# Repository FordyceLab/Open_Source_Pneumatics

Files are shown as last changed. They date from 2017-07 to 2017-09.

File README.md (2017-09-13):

# Open_Source_Pneumatics
An Open-Source, Fully Programmable Pneumatic Setup for Universal Microfluidic Operation and Automated Control

This repository includes Build Guides (All Modules), Build Description and Overview (Manuscript), Customization Options (see Figures), all Design Files (Design File Folder) and a Bill of Materials for 3 build options of an open source microfluidic pneumatic controller. 

We have described this controller in our BioArXiv release which can be found here: 

http://www.biorxiv.org/content/early/2017/08/13/173468

DOI: https://doi.org/10.1101/173468

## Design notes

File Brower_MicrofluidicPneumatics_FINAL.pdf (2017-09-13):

Article Submission: HardwareX Article Template

Title: An Open-Source, Programmable Pneumatic Setup for Operation and Automated Control of Single- and Multi-Layer Microfluidic Devices

Authors: Kara Brower¹,4,5, Robert Puccinelli²

, Craig J. Markin³

, Tyler C. Shimko²

, Scott A. Longwell¹
,
Bianca Cruz⁶

, Rafael Gomez-Sjoberg⁷

*, and Polly M. Fordyce¹,2,4,5,7 *

Affiliations: 1

Department of Bioengineering, ²

Department of Genetics, ³
Department of Biochemistry,

4

Chem-H Institute, ⁵
Stanford Microfluidic Foundry, Stanford University, Stanford CA 94305. 6 Department of Physics and Astronomy, California State Polytechnic University Pomona, Pomona CA 91768. 7
Chan Zuckerberg Biohub, San Francisco CA 94158.

*These authors contributed equally to this work.

Contact email: Polly Fordyce, Ph.D., pfordyce@stanford.edu

Abstract: Microfluidic technologies have been used across diverse disciplines (e.g. high-throughput biological measurement, fluid physics, laboratory fluid manipulation) but widespread adoption has been limited due to the lack of openly disseminated resources that enable non-specialist labs to make and operate their own devices. Here, we report the open-source build of a pneumatic setup capable of operating both single and multilayer (Quake-style) microfluidic devices with programmable scripting automation. This setup can operate both simple and complex devices with 48 device valve control inputs and 18 sample inputs, with modular design for easy expansion, at a fraction of the cost of similar commercial solutions. We present a detailed step-by-step guide to building the pneumatic instrumentation, as well as instructions for custom device operation using our software, Geppetto, through an easy-to-use GUI for live on-chip valve actuation and a scripting system for experiment automation. We show robust valve actuation with near real-time software feedback and demonstrate use of the setup for high-throughput biochemical measurements on-chip. This open-source setup will enable specialists and novices alike to run microfluidic devices easily in their own laboratories.

Keywords: Microfluidics, pneumatics, laboratory automation, biochip, bioMEMs, biohacking, fluid handling, micro total analysis systems (µTAS), Quake-style valves

Specifications table
Hardware name | An Open-Source, Programmable Pneumatic Setup for Operation and Automated Control of Single- and Multi-Layer Microfluidic Devices Geppetto (Python-based solenoid valve control software with GUI) Geppetto CLI (Python-based solenoid valve software with command line scripting for experiment automation)
Subject area | • Engineering and Material Science • Biological Sciences (e.g. Microbiology and Biochemistry) • General

Hardware type | • Biological sample handling and preparation
Open Source License | Pneumatics Instrumentation: GPL License Geppetto Software: MIT License
Cost of Hardware | Variable, dependent on user customization Full Build: $10,380. Abridged Build: $4,455. Manual Build: $2,110. Additional Modification Builds Costs shown in Table 1
Source File Repository | Github: github.com/FordyceLab/Open_Source_Pneumatics Supplementary Materials (In Article)

### 1. Introduction

Microfluidic technologies enable the precise control and manipulation of fluid at the sub-millimeter scale [1]. Simple, single layer microfluidic devices with channels etched in glass or patterned into soft polymers (e.g. polydimethylsiloxane, or PDMS) have facilitated the study of small-scale fluid phenomena, automated sample loading and common laboratory tasks, and been used for high-throughput compartmentalization of biological reactions [2-9]. More complex multilayer microfluidic devices with monolithic soft polymer valves (also known as Quake-style valves [10,11]) have empowered additional research and commercial applications, including on-chip cell culture and tissue engineering [12], crystallization condition scanning [13-15], single cell analysis [16-18], high-throughput biochemical analysis [19-21], hydrogel engineering [22-24], and complex fluid handling tasks [11,25].
These multilayer microfluidic devices are typically fabricated in a two-layer geometry, where each layer is made by conventional soft lithography [10]. The ‘flow layer’ contains channels to load and transport samples. The ‘control layer’ contains a series of channels that create and control pneumatically-actuated valves. The two layers are separated by a thin polymer membrane. A valve is formed when flow and control channels of an appropriate size and shape cross [26]. When a control channel is pressurized, the thin membrane deflects into the crossing flow channel to modulate its flow. Both layers require their own set of input lines to interface with on-chip inlets. For complex chips with many control valves, a computer-controlled bank of solenoid valves is typically used to automate control of applied pressure to the valves.
While multilayer devices can serve as powerful tools for a broad range of biological systems [5,27-29], their widespread adoption has been limited, likely because few detailed open-source protocols and designs for building an automated pneumatic control systems have been published [3,30,31]. Previously, our group worked in conjunction with the Stanford Microfluidic Foundry to publish an open protocol that describes in detail how to fabricate custom multilayer microfluidic devices [32]. In this report, we continue the project of disseminating how-to knowledge on microfluidics by offering designs and detailed step-by-step build instructions for a flexible pressure-driven pneumatic setup that can control both fluid flow and integrated on-chip valves.
The primary pneumatics control system described here allows for automated, programmable control of single and multi-layer microfluidic devices with 48 control lines and 18 individually-addressable flow lines. We present customization options and instructions to build setups from 8 – 96 control lines and 6 – 48 flow lines using this base build. This setup confers several advantages to commercial alternatives including:
- flexible application programming and automation
- remote control to allow experiments to be controlled and monitored outside the lab
- extremely fast valve response times (using Modbus-pulsed solenoid valves)
- very low cost-per-input ratios (both control and flow channel inputs)

The build is modular and easy to customize for a user’s specific needs. We present two modified builds in a later section of the paper for lower complexity control, including a low-cost fully manual control configuration. Previous versions and variants of this setup, originating from the early days of the Stanford Microfluidic Foundry [33], have been used in tens of laboratories resulting in over a hundred peer-reviewed publications ([12,20-23,34,35] are some examples). However, full build details have never been published. Here, we describe the latest optimization of the pneumatic control system in detail to provide a complete tool kit that will allow even labs with little engineering expertise to build all of the instrumentation required for automated microfluidic control.

### 2. Hardware description

The open-source pneumatic setup and software (Figure 1) described here can be used for both manual and fully programmable pneumatic control of most PDMS-based microfluidic devices. Our associated software, Geppetto, has both an interactive GUI for manipulating device valves and visualizing their current state (open or closed) as well as command line scripting functionality for automating experiments.
We present 3 build options for the microfluidic pneumatic control system, as listed below. This setup can additionally be expanded for up to 96 control lines and up to 48 flow lines. Control inputs need not correspond to the actual number of valves on the device - only the number of valves needing independent actuation. Typical multilayer microfluidic devices operate with 10 – 15 control lines and 10 – 15 sample lines, even for complicated tasks, but this build can accommodate devices with more or fewer inputs or the need to run multiple devices simultaneously on the same setup.

### 2.1. Build Options

In this paper, we present 3 options for building a microfluidic pneumatic setup:

Option 1: A full build for 18 flow lines and 48 individually addressable solenoid valves to drive 48 control lines for fully automated, programmable and remote operation of complex devices or multiple devices

Option 2: An abridged build for 6 flow lines and 8 individually addressable solenoid valves to drive 8 control lines for fully automated, programmable and remote operation of simpler devices

Option 3: A low-cost build for manual control of 18 flow lines and 12 control lines

The main text will describe the build for Option 1. The build is modular and can be easily modified to the simpler builds of Options 2 and 3 to reduce time and cost, if only limited or manual control of microfluidic devices is needed.

### 2.2. Module Overview

The pneumatics control system is built in 5 Modules which are divided by manual and automated control capabilities. Options 1 and 2 require all 5 Modules. The manual build, Option 3, requires a modified version of only Modules 1 and 2. The builds for Options 2 and 3 are presented in a Modifications and Customization Section.

The Modules are as follows:

- Module 1: Base Board, Pressure Regulator Manifolds, and Flow Lines
- Module 2: Filter Assembly
- Module 3: Control Solenoid Valve Manifolds
- Module 4: Control Reservoir Loading Assembly
- Module 5: Digital Modbus Control

Manual Control Modules

This pneumatic setup employs pressure-driven flow control. Microfluidic devices, in general, can be operated either by pressure-drive flow (using constant pressure at the input) or volumetric flow (forcing a set flow rate at the input, as a syringe pump does). Volumetric flow results in unknown pressures inside the flow channels, which makes it difficult to ensure that on-chip valves close reliably and can lead to device delamination. This setup uses pressure-driven flow because it requires little additional equipment beyond common laboratory compressed air sources and provides robust valve actuation on-chip.

Controlling pressure-driven flow rates and actuating on-chip pneumatic valves requires a device-specific pressure range: too little pressure and valves don’t close properly, too much pressure and devices can delaminate or become otherwise damaged. Compressed air (from a house air supply, cylinder or compressor) provides a convenient and quiet pressure source but must be adjusted to the correct pressure for microfluidic devices using regulators. Module 1 (Base Board, Pressure Regulator Manifolds, and Flow Lines) describes the base build for the pneumatic assembly to control input pressures. It contains a base board that mounts regulators for controlling both flow lines and control line manifold pressures as well as fluidic components for sample introduction or manual control of integrated on-chip valves.

Module 2 describes how to connect a filtering assembly to the compressed air source to prevent device contamination and/or clogging of the air regulators.

Automated Control Modules

Automation of microfluidic valve actuation enables a wide range of additional assays and remote device control but requires additional control hardware. To control on-chip valves, we employ 24V, three-way, normally open solenoid valves which toggle between an ‘open’ pressurized state (with pressure from the control manifold regulators in Module 1) and a ‘closed’ atmospheric pressure state to close or open on-chip valves, respectively. These solenoid valves are used to pressurize or depressurize water within a reservoir directly connected to control lines, thereby providing individually-addressable control of each control line. Groups of eight of these solenoid valves are coupled to a plastic manifold containing eight water reservoirs connected to eight chip control lines. We call this assembly a control manifold; these manifolds are built in Module 3 (Control Solenoid Valve Manifolds). Module 4 (Control Reservoir Loading Assembly) adds on a large volume water bottle for easy loading and refilling of the water reservoirs in the control manifold. Finally, Module 5 (Digital Modbus Control) describes the electrical connections between the solenoid valves and a microcontroller (the ‘WAGO’ fieldbus controller) to allow values to be digitally controlled by the user via a computer.

Pneumatic Control System Operation

Combined, these modules constitute all the components and connections necessary to provide pressure-driven flow control and actuate integrated on-chip valves of microfluidic devices. Initial setup of the system for experimental use is described in the Operation Device Guide.

Figure 1. Photograph of a completed pneumatic build (Option 1) with all 5 build modules.

Figure 2. Overall setup schematic with parts designated by letter and number (as referenced to the Bill of Materials).

While at first glance this setup may seem complicated, we have built multiple setups with researchers of all technical backgrounds with little to no engineering training. Each module is accompanied by a schematic, parts list and illustrated step-by-step build instructions (Build Guides) that are included in the Supplemental Material of this report. The total build takes 1.5 days from start to device testing and is easily managed with 1-2 researchers and common laboratory tools.

2.3.Advantages of an Open-Source Build

Building an open-source pneumatic microfluidic control system has three main advantages to both academic researcher and small companies. First, open source builds are flexible and can be easily modified for a laboratory’s needs [30,36]. For instance, this paper describes two easily modified options from the base build in the Modification and Customization Section. Second, this build is highly modular; if a component fails or the user prefers a different alternative to a given module (i.e., using an Arduino as opposed to a WAGO PLC), parts can easily be swapped or exchanged. This can be contrasted with commercial closed-source pumps and instruments where exchanges and repairs are often costly and time-consuming. Lastly, the control system described here is significantly cheaper per input than existing solutions, as discussed below.

2.4.Note on Associated Build Costs

This setup has a significantly reduced cost compared to commercial alternatives for the same number of independent input controls. Table 1 shows the cost of hardware for Build Option 1 (full build, 48 control lines), Build Option 2 (modified programmable build, 8 control lines) and Build Option 3 (fully manual, 12 control lines). The most expensive components are the solenoid valve arrays and WAGO fieldbus digital control modules, which scale directly with the number of independently-addressable control lines needed, as shown in Table 1. While the cost of these programmable setups can be significant ($4,455 to $10,380 dependent on number of inputs), commercial solutions cost between $1,500 (lower-end microfluidic syringe pumps) to $5,550 (high end pressure-driven pumps, e.g. Dolomite P-PumpTM) per independent input. Consequently, obtaining a similarly programmable pneumatic system for many inputs from commercial suppliers would be > 10X more expensive in the current market than the build described here.

Build Option | Cost of all associated hardware
#1: Full Programmable Build (48 control lines, 18 flow lines) | $10,379.65

#2: Abridged Programmable Build (8 control lines, 6 flow lines) | $4,455.14

#3: Manual Build (12 control lines, 18 flow lines) | $2,110.50

Table 1 Cost of Hardware for the different Build Options. See Supplemental Bill of Material for itemized costs.

2.5.Hardware Summary

- This build describes a pressure-driven pneumatic setup for single- and multi-layer microfluidic device operation. Devices can be operated manually or digitally, enabling remote control.
- The user can customize the number of flow inputs (up to 48) and the number of control inputs (up to 96) for their application.
- The associated software for digital valve control, Geppetto, includes a GUI for fast valve actuation and visualization of current valve states as well as an easy way to script experiments for automated control.
- The build description includes design files to be cut, printed, or machined, as well as overview instructions and step-by-step build guides to construct the setup in 5 different modules, a bill of materials and individual parts list by module, software operation instructions, and an example case for easy construction. These resources can also be found on our Github (https://github.com/FordyceLab/Open_Source_Pneumatics).
- The final setup is ~48” x 24” including the control computer and can be mounted on an optical breadboard, lab bench, or any workspace with either screws or C-clamps.

### 3. Design Files

3.3.Design Files Summary

The following design files are necessary to complete this build. Downloads of parts in editable file formats (e.g. AutoDesk 360 files) are available on the GitHub repository under the Designs folder.

Design file name | File type | Open source license | Location of the file
System Schematic | PDF | GPL | Available with the article
Bill of Materials, Detailed with Links | XLSX | GPL | Available with the article
Build Guides | PDF (multiple) | GPL | Available with the article
Base Board (backboard-full) | PDF DXF | GPL | Github:github.com/FordyceLab/Open_Source_Pneumatics
Flow Control Manifolds (stopcock-mount) | STL | GPL | Github:github.com/FordyceLab/Open_Source_Pneumatics
Water Reservoir Stand (reservoir-stand) | PDF DXF STL | GPL | Github:github.com/FordyceLab/Open_Source_Pneumatics
Control Water Reservoir (reservoir) | PDF DXF | GPL | Github:github.com/FordyceLab/Open_Source_Pneumatics
Geppetto Geppetto CLI | Python code | MIT | Github: https://github.com/FordyceLab/geppetto Github: https://github.com/FordyceLab/geppetto-cli

Table 2 Design File Summary.

3.4.Description of Design Files

Build Instructions

System_schematic_pneumatics.pdf – Schematic of all parts organized by build module Bill_of_Materials_pneumatics.xlxs – Multi-sheet parts list, global and by-module (includes modification and custom build Options 2 and 3).

Build and Operation Step-by-Step Guides
Module_1_Base_Build_Guide.pdf – Guide for the Module 1 build Module_2_Filter_Assembly_Guide.pdf – Guide for the Module 2 build Module_3_Valve_Manifolds_Guide.pdf – Guide for the Module 3 build Module_4_Control_Loading_Guide.pdf – Guide for the Module 4 build Module_5_WAGO_Guide.pdf – Guide for the Module 5 build
Operation_Start_Guide.pdf – Instructions for setup initialization and first-time use. Device_Operation_Guide.pdf – Instructions for device operation and experimental automation.

Laser Cut Parts
Base Board: backboard-full (PDF specifications; DXF for submission to 3rd party) – 28” x 20” backboard to which most components are mounted. Fabrication: ¼” aluminum or acrylic stock. Holes can be drilled or laser cut. Threaded holes hand-tapped as per specifications.
Water Reservoir Stand: reservoir-stand (PDF specifications; DXF for submission to 3rd party; STL for 3D printing) – Mounting stand for control manifold water reservoirs. Fabrication: ¼” aluminum or acrylic stock. Threaded holes hand-tapped as per specifications. Alternatively, can be ordered from local plastic suppliers/3rd party, or 3D printed on printers with a sufficiently large workspace.

Optional Modified Laser Cut Parts
Base Board Alternatives:

backboard-left (PDF specifications; DXF for submission to 3rd party) – The left 10.5” of backboard-full. Its reduced size enables fabrication on laser cutters with smaller workspaces. It should be used with backboard-right; if this component is used, backboard-full is not needed. backboard-right (PDF specifications; DXF for submission to 3rd party) – The right 17.5” of backboard-full. Same specifications as above.
backboard-left-lc (PDF for laser cutter) – Variation of backboard-left specifically for direct conversion to a Universal Laser Systems file format (lines are 0.02 mm wide, [255,0,0] RGB). Please verify that the file format is compatible with your laser cutter.
backboard-right-lc (PDF for laser cutter) – Variation of backboard-right specifically for direct conversion to a Universal Laser Systems file format (lines are 0.02 mm wide, [255,0,0] RGB). reservoir-stand-lc (PDF for laser cutter) – Variation of reservoir-stand specifically for direct conversion to a Universal Laser Systems file format (lines are 0.02 mm wide, [255,0,0] RGB).

Machined Parts
Control Water Reservoirs: reservoir (PDF specifications; DXF for submission to 3rd party) – Control manifold reservoirs used to hold water for control lines. Fabrication: 1” acrylic stock. Custom machined in-house or by 3rd party.

3D Printed Parts

Flow Control Manifold: stopcock-mount (STL for printing) – Mount for 3 stopcocks that control flow line pressurization. Fabrication: ABS plastic or similar.

Open-Source Software
Geppetto (Github Repository) – Python pneumatic control software with Kivy GUI and optional Windows binary. A Read Me file and all code dependencies are included in the repository unless noted. Example files are included in the repository.

Geppetto CLI (Github Repository) – Python pneumatic control software for command line scripting (command line integration, CLI) to automate experiments. A Read Me file and all code dependencies are included in the repository. Example files are included in the repository.

### 4. Bill of Materials

4.3.Master Bill of Materials

The following is a global list of materials to be purchased before the build. Material quantities should be adjusted to the needs of your build. The main build (Build Option 1) used as an example in the following Build Guides is for 18 flow line inputs and 48 individually-addressable control line inputs. Materials lists for modified Build Options 2 and 3 are presented in the Modification and Customization Section.
GLOBAL REQUIREMENTS BY MODULE FOR FULL BUILD

Table 1: Global Tubing Requirements

Component | Source | Catalog Number | Quantity | Cost /Unit | Total | Part
1/4" OD x 1/8" ID polyurethane tubing, blue, 50 ft roll | McMaster-Carr | 5648K74 | 1 | $29.00 | $29.00 | T1
1/4" OD x 1/8" ID Tygon tubing, clear, 50 ft roll | McMaster-Carr | 6516T14 | 1 | $40.50 | $40.50 | T2
5/32" OD x 3/32" ID polyurethane tubing, clear, 100 ft roll | Pneumadyne | PU-156F-0 | 1 | $17.00 | $17.00 | T3
3/16" OD x 1/8" ID Tygon tubing, opaque, 50 ft roll | Grainger | 2LPR9 | 1 | $17.41 | $17.41 | T4
Tygon ND-100-80 Tubing (500' roll, 0.06" OD, 0.02" ID) | Fisher Scientific | 14-171-284 | 1 | $317.00 | $317.00 | T5
Spirally-Cut Cable Wrap, 3/8" O.D., Black Polyethylene | M.M. Newman Corp. | HT 3/8 UR-25 | 1 | $14.98 | $14.98 | T6

Table 2: Pneumatic Control System, Module I: Base Board, Pressure Regulator Manifolds, and
Flow Lines
Component | Source | Catalog Number | Quantity | Cost /Unit | Total | Part
Double Standard Solid 80/20 Rails (26" x 2" x 1") | McMaster-Carr | 47065T803 | 2 | $21.06 | $42.12 | b1
Single Standard Solid 80/20 Rails (26" x 1" x 1") | McMaster-Carr | 47065T848 | 3 | $9.36 | $28.08 | b2
Double Standard Hollow 80/20 Rails (12" x 2" x 1") | McMaster-Carr | 47065T107 | 2 | $9.13 | $18.26 | b3
Diagonal 80/20 Rail (6" x 1" x 1") | McMaster-Carr | 47065T186 | 2 | $15.67 | $31.34 | b4
Standard End Feed Fasteners, Pack of 4 | McMaster-Carr | 47065T142 | 6 | $2.30 | $13.80 | b5
Elbow Bracket 4-Hole Extended Corner Bracket | McMaster-Carr | 47065T239 | 8 | $5.85 | $46.80 | b6
Extended Corner 8-Hole Fastener | McMaster-Carr | 47065T253 | 2 | $8.79 | $17.58 | b7
Corner 5-Hole Surface Bracket | McMaster-Carr | 47065T267 | 2 | $8.47 | $16.94 | b8
10-32 1/2" Socket Head Screws, Pack of 100 | McMaster-Carr | 91251A342 | 1 | $9.60 | $9.60 | s1
6/32 1-1/2" Partially-Threaded Socket Head Screws, Pack of 50 | McMaster-Carr | 91251A157 | 1 | $9.94 | $9.94 | s2
6-32 1/4" Socket Head Screws, Pack of 100 | McMaster-Carr | 91251A144 | 1 | $8.46 | $8.46 | s3
SMC Precision Air Regulator, 1/4" ports, 60 psi upper range | Stevens Engineering | IR2010-N02 | 3 | $75.80 | $227.40 | A
Pressure Gauge, 1/4" Back Connector, 0-60 psi | McMaster-Carr | 4000K791 | 3 | $12.03 | $36.09 | B
1/4" NPT to 1/4" Brass Push-to-Connect Tube Fitting | McMaster-Carr | 7880T125 | 16 | $2.24 | $35.84 | C
Brass Tee Fitting, 1/4" NPT, FxFxM | McMaster-Carr | 50785K222 | 6 | $4.90 | $29.40 | D
Brass Elbow Fitting, 1/4" NPT, FxM | McMaster-Carr | 50785K43 | 6 | $2.50 | $15.00 | E
Precision Air Regulator, 1/4" ports, 30 psi lower range | Stevens Engineering | IR2000-O2-A | 3 | $75.80 | $227.40 | F
Digital Pressure Gauge, 1/4" MNPT, 0-30 psi | McMaster-Carr | 3943K15 | 3 | $428.45 | $1,285.35 | G
Male Luer Integral Lock Ring, 400 series, 1/8" barb, Pack of 100 | Value Plastics | MTLL430-9002 | 1 | $20.20 | $20.20 | H
1-Way Luer Stopcock, M Lock, Pack of 100 | Cole-Parmer | Sk-30600-05 | 1 | $185.00 | $185.00 | I
Female Luer 1/4"-28 Panel Mount to 1/8" Barb, Pack of 100 | Value Plastics | FTLLB230-1 | 1 | $19.00 | $19.00 | J

Tee Tube Fitting for 1/8" ID Tubing, Pack of
100 | Value Plastics | T230-1 | 1 | $26.80 | $26.80 | K
Luer Plug Caps, Pack of 10 | McMaster-Carr | 51525K311 | 1 | $2.41 | $2.41 | L
Male Luer Integral Lock Ring, 1/8" barb, Pack of 100 | Value Plastics | MTLL230-9 | 1 | $20.20 | $20.20 | M
4-Way Luer Stopcock, M Lock, F Connectors, Pack of 100 | Cole-Parmer | EW-30600-09 | 1 | $185.00 | $185.00 | N
Blunt Stainless Steel Luer Lock Needle, Pack of 50 | McMaster-Carr | 75165A684 | 1 | $11.88 | $11.88 | O
4 -Station Control Manifold, 1/4" NPT-F inlets, 1/8" NPT outlets | Pneumadyne | M10-125-4 | 2 | $12.60 | $25.20 | P
Dented Toggle Control Switch, 1/8" NPT input, 10/32" output | Pneumadyne | C030621 | 8 | $14.06 | $112.48 | Q
10-32 UNF to 1/4" Push-to-Connect Tube Fitting | McMaster-Carr | 7880T122 | 8 | $3.31 | $26.48 | R
1/4" Push-to-Connect Plug | McMaster-Carr | 5779K54 | 2 | $1.16 | $2.32 | S

Table 3: Pneumatic Control System, Module 2: Filter Assembly to House
Air
Component | Source | Catalog Number | Quantity | Cost /Unit | Total | Part
3-Way 1/4" Push-to-Connect Manifold | McMaster-Carr | 5779K318 | 2 | $16.60 | $33.20 | T
1/4" NPT to 1/4" Brass Push-to-Connect Tube Fitting | McMaster-Carr | 7880T125 | 2 | $2.24 | $4.48 | C
Brass Ball Valve, T-handle, 1/4" NPT FxM | McMaster-Carr | 4912K92 | 1 | $7.02 | $7.02 | U
Wilkerson Modular Compressed Air Filter, 5 um, 1/4" Connector | McMaster-Carr | 60115K19 | 1 | $70.27 | $70.27 | V
Filter Joiner Clamp | McMaster-Carr | 60115K22 | 1 | $13.05 | $13.05 | X
Standard Oil vapor and Odor Removal Filter, 0.003 um | McMaster-Carr | 7426K11 | 1 | $80.10 | $80.10 | Y
Brass Elbow Fitting, 1/4" NPT, FxM | McMaster-Carr | 50785K43 | 1 | $2.50 | $2.50 | E
1/4" Push-to-Connect Plug | McMaster-Carr | 5779K54 | 1 | $1.16 | $1.16 | S

Table 4: Pneumatic Control System, Module 3: Control 8-Valve
Solenoid Manifolds

Component | Source | Catalog Number | Quantity | Cost /Unit | Total | Part
4-Way Luer Stopcock, M Lock, F Connectors, Pack of 100 | Cole-Parmer | EW-30600-09 | 0 | $185.00 | $0.00 | N
10-32" Special Tapered Thread to Male Luer w 1/4" Hex, Pack of 100 | Value Plastics | XMLRL-9 | 1 | $34.80 | $34.80 | a
Finger Snap Luer Lock Ring, Pack of 100 | Value Plastics | FSLLR-9002 | 1 | $14.50 | $14.50 | b
Male Luer to Barb Elbow, 1/8" ID Tubing, Pack of 100 | Value Plastics | LE7230-9 | 1 | $50.40 | $50.40 | c
Luer Adapter, Pair to Female 1/4"-28 | Idex | P-628 | 48 | $3.90 | $187.20 | d
Flangeless Ferrule (ETFE), 1/4"-28 Flat-Bottom, Pack of 25 | Idex | P200 | 2 | $32.75 | $65.50 | e
Flangeless Male Nut, 1/4"-28 Flat-Bottom, 1/16" OD Red, Pack of 25 | Idex | P202 | 2 | $32.75 | $65.50 | f
1/4" to 5/32" NPTF-M Push-to-Connect | McMaster-Carr | 51055K8 | 48 | $1.99 | $95.52 | g
Luer Plug Caps, Pack of 10 | McMaster-Carr | 51525K311 | 0 | $2.41 | $0.00 | L
Steel Blunt Pins, 1/2" length, Pack of 250 | NE Small Tube | NE-1310-02 | 1 | $212.50 | $212.50 | P1
Tee Tube Fitting for 1/8" ID Tubing, Pack of 100 | Value Plastics | T230-1 | 0 | $26.80 | $0.00 | K
8-Valve Solenoid Valve Manifold | Festo | MH1A24VDCN HC8VPRK01QM APBPCXDX | 6 | $564.71 | $3,388.26 | h

Table 5: Pneumatic Control System, Module 4: Control
Loading
Component | Source | Catalog Number | Quantity | Cost /Unit | Total | Part
Male Luer Integral Lock Ring, 1/8" barb, Pack of 100 | Value Plastics | MTLL230-9 | 0 | $20.20 | $0.00 | M
Female Luer 1/4"-28 Panel Mount to 1/8" Barb, Pack of 100 | Value Plastics | FTLLB230-1 | 0 | $19.00 | $0.00 | J
Nylon 1/4"-28 Hex Nut, Pack of 100 | McMaster-Carr | 94812A800 | 1 | $6.47 | $6.47 | i
Scientific Nalgene Polypropelene Wide Mouth Bottle | Cole-Parmer | EW-06057-10 | 1 | $26.36 | $26.36 | j
Luer Lock Manifold, 5 Ports, F Luer, Pack of 10 | Cole-Parmer | EW-30600-43 | 1 | $95.00 | $95.00 | k

1-Way Luer Stopcock, M Lock, Pack of 100 | Cole-Parmer | Sk-30600-05 | 0 | $185.00 | $0.00 | I

Male Luer Integral Lock Ring, 1/8" barb, Pack
of 100 | Value Plastics | MTLL430-9002 | 0 | $20.20 | $0.00 | H

Table 6: Digital Modbus Control

Component | Source | Catalog Number | Quantity | Cost /Unit | Total | Part
WAGO Programmable I/O Controller | WAGO | 750-881 | 1 | $665.00 | $665.00 | W1
WAGO AC/DC DIN Rail Power Supply, 240W | WAGO | 787-732 | 1 | $135.00 | $135.00 | W2
WAGO 4-channel digital output, 24 V, 0.5 A | WAGO | 750-504 | 14 | $72.22 | $1,011.08 | W3
WAGO I/O End Module | WAGO | 750-600 | 1 | $20.00 | $20.00 | W5
Mounting Rail, DIN 3 Rail, 35 mm wide, 1 m long | McMaster-Carr | 8961K15 | 1 | $5.07 | $5.07 | W6
Ethernet Cable , CAT5E | Digikey | AE10492-ND | 1 | $4.66 | $4.66 | m
8 ft. Power Cord with SPT-1 NEC Cord | Grainger | 1FD95 | 1 | $7.76 | $7.76 | n
Assorted Wire, Red and Black, 18G | Amazon | SW18A08F5C2 | 1 | $5.98 | $5.98 | o

Table 7: Machined Part Cost Estimates

Baseboard (backboard, laser cut acrylic) | Laser Cut, TAP Plastics | 1 | $110.77 | $110.77 | -
Flow Control Manifolds (stopcock-mount, 3D printed ABS) | 3D Printed, uPrint | 6 | $12.00 | $72.00 | -
Water Reservoir Stand (reservoir-stand, laser cut acrylic) | Laser Cut, Big Blue Saw | 6 | $14.38 | $86.28 | -
Control Water Reservoir (reservoir, machined acrylic) | Machined | 6 | $105.00 | $630.00 | -
OPTION 1 FULL BUILD | TOTAL | $10,379

Table 3 Full Build (Build Option 1) Bill of Materials by Module. Parts are purchased by Module. Any “0” quantity denotes that a multi-part pack has been previously purchased of sufficient size to provide all additional parts needed for the Module in question. Links to manufacturer sites are included in the Bill_of_Materials_pneumatics.xlxs supplemental file (Supplement 2).

A more detailed Bill of Materials with purchasing links and further information is available as Supplement 2 and is updated often on our Github repository, available here.

### 5. Build Instructions

5.1.Overview of Multi-Component Build

This build takes place in 5 discrete modules that eventually interconnect. The following general build schematic describes all the parts and connections necessary to complete the build (Figure 2). For each module, we describe the module operation and provide a ‘close up’ version of the schematic compared to the final implementation of that assembly. Assembly details are presented step-by-step in detail in a series of 5 build guides in the Supplemental Information of this article. The end result will be a pressure-driven pneumatic setup for automated device control that is ready to use.

The following sections describe the details for the main Build Option 1. These sections can be used as examples for Build Options 2 and 3 but will need to be adjusted accordingly to the schematics presented for those options, as shown at the end of this paper.

5.2.Module 1: Base Board, Pressure Regulator Manifolds, and Flow Lines

This module describes the main base build for the setup. Each build has air regulators to control the pressures used to drive manual flow and valve lines. As different on-chip flow inputs may require different pressures, the board contains several different ‘flow’ regulators to control pressures to the flow line manifolds mounted on the base board (right side regulators). In the main build, 3 regulators control 18 flow lines as shown in Figure 2. Digital gauges provide highly precise low-range (0-20 psi) flow control and are powered by the WAGO modus controller described in Module 5. The manual build, Build Option 3, replaces these digital gauges with low-range (0-10 psi) analog gauges for a cost-effective alternative, with some sacrifice to measurement precision.
For automated builds (Builds 1 and 2), regulators also supply pressure for the banks of control solenoid valve manifolds that ultimately pressurize the control lines and actuate on-chip microfluidic valves (left side upper regulators). In the main build, 2 regulators control pressurization of the control solenoid manifolds and modulate their pressurization via mounted switchboxes (left side). These switchboxes connect directly to the 8-valve manifolds presented in Module 3. The regulators used here can be relatively imprecise as long as they provide pressure regulation in the range needed to close microfluidic devices (0-60 psi). Manual versions are sufficient. Automated builds further have an integrated option to load and refresh the control manifold valve banks with water easily. In the main build, a regulator (left side bottom regulator) is dedicated to this task and connected to the control loading assembly in Module 4. These components are mounted to a single base plate for convenient adjustment and connection between modules. The build guide provides instructions on how to mechanically connect all components to the base plate and pneumatically connect components to one another.

Figure 3. (a) Module 1 schematic. (b) Finalized implementation of Module 1.

To build this module, follow the Module_1_Base_Build_Guide.pdf (Supplement 3).

5.3.Module 2: Filter Assembly

This module inserts a filter assembly between the compressed air source and the regulators on the Base Board (Module 1) to keep oil or small particulates in the pressurized air from contaminating the regulators and on-chip valves in critical experiments (e.g. long-term cell culture or on-chip enzymatic assays). This assembly can be replaced by cheaper disposable filters if desired.

Figure 4. (a) Module 2 schematic. (b) Finalized implementation of Module 2.

To build this module, follow the Module_2_Filter_Assembly_Guide.pdf (Supplement 4).

5.4.Module 3: Control 8-Valve Solenoid Manifolds

This module creates the hardware necessary for automated valve actuation. The main build has 6 sets of Control Valve Manifolds that actuate on-chip valves by pressurizing water-filled Tygon control lines connected to on-chip control channels. Each Control Valve Manifold has 8 water reservoirs connected to 8 solenoid valves with independent actuation. Each solenoid valve is individually driven by a 24V signal supplied by the fieldbus controller of Module 5. When actuated, each solenoid pressurizes a water reservoir (pressure sent from the Base Board – Module 1) and its connected control line input to the microfluidic device to close dead-end valves. The water reservoirs also have a loading function (via a separate fluidic circuit activated by toggling the manifold stopcocks) so that water can be refreshed via Module 4.
Fast valve pressurization is often critical for many microfluidic assays including on-chip biochemical assays, droplet generation, microfluidic sorting and precise fluidic dosing using on-chip pumps [20,22-24,35]. The Festo 24V solenoid valves used here, while expensive, offer superior response times essential for fast valve actuation as well as reliable state switching with long lifetime (>5 years operation). The response times of these solenoid valves is ~ 4 ms response from pulse. Full fluidic valve actuation on-chip from the digital pulse is on the order of 7-20 ms, dependent on valve and device geometry. The three-way, normally-open solenoid valves in this setup toggle between atmospheric pressure and compressed air as set by the regulators of Module 1, allowing lines to be vented to atmosphere when not in use (two-way valves lack the ability to vent lines or depressurize lines to open valves). The use of normally-open solenoid valves allows on-chip valves to return to a safe ‘closed’ position in the event of an unexpected software crash or power interruption. In addition, these valves are additional very low profile, easily allowing parallelization as demonstrated in this build.
To customize the build, control lines can be filled with oil or buffer instead of water to reduce osmotic water transfer between control and flow lines. Three-way solenoid valve arrays can also be connected to other air sources to toggle between different states (e.g. vacuum and compressed air, vacuum and atmospheric pressure – instead of atmospheric pressure and compressed air), if needed.

Figure 5. (a) Module 3 schematic. (b) Finalized implementation of Module 3.

To build this module, follow the Module_3_Valve_Manifolds_Guide.pdf (Supplement 5).

5.5.Module 4: Control Reservoir Loading Assembly

Maintaining water in the water reservoirs is essential for properly pressurizing control lines as air within the lines can create uneven closing times across the devices and nucleate bubbles in the flow channel in long-term experiments. This module builds a pressure vessel and associated tubing for loading water into the water reservoirs of the Control Valve Manifolds from Module 3 to prevent control line drying. While loading the water reservoirs can be completed without this pressure vessel assembly (e.g. using tubing), this assembly simplifies the water loading process. Water is loaded by pressurizing the water vessel (driven from a regulator in Module 1) and switching the relevant manifold stopcock so that water flows into the manifold. Further details can be found in the Device Operation Guide.

Figure 6. (a) Module 4 schematic. (b) Finalized implementation of Module 4.

To build this module, follow the Module_4_Control_Loading_Guide.pdf (Supplement 6).

5.6.Module 5: Digital Modbus Control

This module adds computer-based control of valve actuation. A WAGO programmable logic controller (“Fieldbus controller”) is used to send 24V pulses to actuate the solenoid valves of Module 3 individually, as well as power the digital gauges of Module 1 (note: these gauges can be powered without the WAGO, but the WAGO provides a convenient integration of all electronic components in this context). The WAGO controller accepts a wide variety of input/output modules (“brick modules”) to create flexible and scalable control systems. The build presented here includes a power supply module for global power and ground, the WAGO controller CPU module with Ethernet connectivity, a series of 24V digital output (DO) modules for controlling valve states, and a 5V output module for powering auxiliary devices (e.g. digital gauges or hardware requiring TTL inputs). A computer can communicate with the WAGO fieldbus controller over Ethernet using a standard protocol called MODBUS. These communications are abstracted from the user using our Geppetto GUI or CLI software. Full wiring and computer setup details are reviewed in the Build Guide for this module.
For project-specific customization, it should be noted that the 4-way DO modules we have chosen send out digital signals that switch between 0V (float) and 24V (high-side control). Modules for more complex tasks such as digital in (DI) or mixed DO/DI modules can be swapped in or out depending on your needs (e.g., for additional equipment control). Alternatives to the WAGO controller (such as Arduino PLCs, presented by White and colleagues in this issue [ref]) can be used but current and voltage compatibilities with the Festo solenoids should be checked before wiring.

Figure 7. (a) Module 5 schematic. (b) Finalized implementation of Module 7.

To build this module, follow the Module_5_WAGO_Guide.pdf (Supplement 7).

WAGO Global Setting | File type
WAGO Ethernet Dip Switch | 198.168.1.3
Connection Watchdog Timer (Ethernet) | 0 (timer off)

Table 4 WAGO global settings for this implementation.

### 6. Modification and Customization

The pneumatic setup outlined here can easily be customized for your laboratory’s needs. Each component is highly modular, enabling easy part exchanges. Our Build Guides contain useful advice on our own trials using different part alternatives, when applicable. To demonstrate the ability to modify the base build, we present two additional build options with accompanying schematics. To build these options, simply use the previous Build Guides as needed for each part; component installation is exactly the same. The fully manual build, Build Option 3, does not use Modules 3, 4, or 5.

Option 2: An abridged build for 6 flow lines and 8 individually addressable solenoid valves to control 8 control lines that fully automated, programmed and remotely operated for simpler devices

Figure 8. Build Option 2 Schematic.

To build this option, follow the Option 2 Build Materials List (Supplement 2, Bill of Materials Sheet 2).

Option 3: A fully manual build for 18 flow lines and 12 manually addressable control lines without automation capabilities which can be used to save costs

Figure 9. Build Option 3 Schematic.

To build this option, follow the Option 3 Build Materials List (Supplement 2, Bill of Materials Sheet 3).

### 7. Operation Instructions

After completing the build, it is now time to begin the exciting process of testing and operating the first microfluidic device with your new setup! Before beginning, follow the initialization guide Operation_Start_Guide.pdf (Supplement 8) to pressurize and check for leaks in the system.

7.1.Geppetto: Python Operation and Scripting

We recommend operating your microfluidic device using our pneumatic control software, which enables valve state visualization and control as well as scripting. Alternatively, users can write their own MODBUS implementation for talking to the WAGO, if desired. Geppetto is a Python-based pneumatic control software built using the Kivy graphical user interface framework for GUI development. Geppetto’s GUI supports nearly any user-defined control layout, with the ability to change the background image and the placement of the control buttons to match any user-designed device using a simple YAML config file.

To customize Gepetto for your own microfluidic device, use the Read Me under our Github release available at https://github.com/FordyceLab/geppetto. If you are unfamiliar with Python, an excellent tutorial can be found here on how to install and operate Python on your machine.

Figure 10. Example Geppetto GUI for valve state visualization of a microfluidic device. Shown here is the custom GUI configured for the MITOMI demo device (see Section 9).

After installing Geppetto, load an image of the device design according to instructions in the Read Me and adjust valve locations to the correct positions in the image. The final image should look similar to the following (Figure 10).

7.2.Operating a Chip

To operate a microfluidic device, follow the steps Device_Operation_Guide.pdf (Supplement 9).

To summarize:
1. Connect the control lines and flow lines to the device.
2. Pressurize the control and flow regulators to the desired pressures and toggle the control manifold switches to send pressure into the control manifolds.
3. Use Geppetto to actuate the valve states.

We previously published a Jove video protocol of a device run that may be useful for visualization of this process [32].

7.3.Automating Microfluidic Experiments

Geppetto also allows scripting of valve actuation events and wait times to automate microfluidic experiments. Scripting occurs in the command line using the Geppetto CLI program (https://github.com/FordyceLab/geppetto-cli). Use the Read Me to set up your first scripting experiment. Example files (e.g. the script for our example experiment below) can be found under the Scripts folder.

### 8. Validation and Characterization

The pneumatics control setup described here has been used in our laboratory for multiple studies, including the microfluidic generation of hydrogel microparticles [32], microfluidic synthesis of lanthanide-encoded beads [24], and high-throughput biochemical affinity measurements on-chip [35]. Here, we describe an example microfluidic experiment using the full pneumatic build, Geppetto CLI, and a microfluidic device, MITOMI (as described previously [19,20,35]) for high-throughput affinity measurements.

8.1.Confirmation of Multi-valve Pressurization and State Change

Figure 11 shows a brightfield image of multiple valve opening and closing events on chip, with valve state controlled via the Geppetto GUI. Supplement 10 is a video of valve toggling events, demonstrating individually-addressable valve control.

Figure 11. (a) Valve closed state under 25 psi control on a MITOMI device. (b) Valve open state.

8.2.Characterization of Valve Closing Pressures and Response Times for Multiple Device Geometries

We have characterized required microfluidic valve control pressures across a wide range of device geometries. “Push-down” devices (control layer on top) fabricated via standard soft lithography techniques tend to operate at 15-20 psi for complete valve closure. “Push-up” devices (control layer on bottom) can tolerate higher pressures (e.g. these devices are more resistant to delamination) and operate from 10-40 psi (or higher). For a given channel geometry, push-down valves require higher pressures to close than push-up valves [2,10,11]. The appropriate valve closing pressures can be determined by the user for new device geometries by introducing using beads or food dye into the flow channel, varying input pressures, and visualizing whether all the fluid is completely excluded beneath the valve.

8.3.Automating a Microfluidic Experiment

To demonstrate the automation potential of the setup, we scripted an experiment in Geppetto to carry out successful surface patterning of a MITOMI device. MITOMI is a microfluidic device that has been employed for many high-throughput biochemical measurements, most notably for assessing thousands of transcription factor (TF) binding affinities to DNA sequences printed on a glass slide [19,20,35]. MITOMI devices contain hundreds to thousands of individual pairs of chambers with multiple types of valves (e.g. a neck valve for connecting chamber pairs, button valves for patterning specific areas in a larger chamber, and sandwich valves for isolating chambers from one another) for performing biochemical affinity measurements.
In our experiment, we performed a simple multi-step surface functionalization to pattern anti-eGFP in a small circular area in each chamber pair using the ‘button’ valves of the device, which protect the glass surface from interacting with introduced solutions when activated. We automated the experiment using scripting in Geppetto CLI. Our script (Supplement 11) outlines the valve actuation events and flow times. Further details on this experiment program can be found here.
In particular, we created a patterned circle of anti-eGFP antibodies on the glass slide surface in the “push-down” device via the following steps: (1) open button valve, (2) introduce biotinylated BSA,
(3) wash, (4) introduce neutravidin, (5) wash, (6) close button, (7) passivate all surfaces except those beneath the button by introducing more biotinylated BSA, (8) wash, (9) open button, (10) introduce biotinylated anti-eGFP (which is recruited to neutravidin-coated surfaces beneath the button), and (11) wash. Device preparation and setup for this experiment is described in detail as an example in the Device_Operation_Guide.pdf (Supplement 9).
We then tested if the patterning had been successful by flowing eGFP protein over the device (button valves open) followed by washing and then visualizing the resultant fluorescence in the eGFP channel. Surface patterning and immobilization is shown in Figure 13, demonstrating that valve actuation and automated control of sample introduction during the experiment were successfully implemented.

Figure 12. Image of a fully prepped MITOMI device with control lines and flow lines in operation.

Figure 13. Experimental results showing an increase in eGFP under only the button area resulting from precise valve-actuation events for successful patterning.

### 9. Discussion

In this report, we provide instructions on how to build a pressure-driven pneumatic setup for universal microfluidic device operation and automated control. This system is capable of driving 18 flow inputs and 48 individually-addressable control line inputs on a microfluidic chip. The setup build is easily adjustable, scalable, and customizable to a user’s needs while being cost-effective compared to similar commercial solutions. To demonstrate this modularity, we have presented two additional build options,
(1) an abridged programmable setup with fewer control lines and (2) a fully manual setup. With the completion of the build, any user should be able to operate and automate a wide range of microfluidic devices and experiments. This open-source hardware and software build should enable researchers from all fields to take advantage of microfluidic technologies and easily operate their own devices.

### 10. Acknowledgements

The authors acknowledge the Fordyce Lab members, in particular Bianca Cruz, for their helpful comments and feedback on the build revisions and manuscript. This work was supported by NIH/NIGMS grants R00GM09984804, DP2GM123641, and R01GM107132. P.M.F. acknowledges support from the Beckman Foundation, the Sloan Research Foundation, and a McCormick and Gabilan faculty fellowship. P.M.F. is a Chan Zuckerberg Biohub Investigator. K.B. acknowledges support from a TL1 Stanford Clinical and Translational Science Award to Spectrum (NIH TL1 TR 001084) fellowship, a Chemical Biology Interface (CBI) fellowship from the Chem-H Institute (Stanford University) and a NSF GRFP fellowship. C.J. M. acknowledges support from the Canadian Institutes of Health Research (CIHR) postdoctoral fellowship. T.C.S. acknowledges support from a NSF GRFP fellowship. B.C. acknowledges Stanford CAMPARE for support for a summer research rotation at Stanford University.

### 11. References

[1] G.M. Whitesides, The origins and the future of microfluidics, Nature. 442 (2006) 368–373. doi:10.1038/nature05058.
[2] J. Melin, S.R. Quake, Microfluidic Large-Scale Integration: The Evolution of Design Rules for Biological Automation, Annu. Rev. Biophys. Biomol. Struct. 36 (2007) 213–231. doi:10.1146/annurev.biophys.36.040306.132646.
[3] D. Mark, S. Haeberle, G. Roth, F. von Stetten, R. Zengerle, Microfluidic lab-on-a-chip platforms: requirements, characteristics and applications, Chemical Society Reviews. 39 (2010) 1153–1182. doi:10.1039/b820557b.
[4] T.A. Duncombe, A.M. Tentori, A.E. Herr, Microfluidics: reframing biological enquiry, Nat. Rev. Mol. Cell Biol. 16 (2015) 554–567. doi:10.1038/nrm4041.
[5] E.K. Sackmann, A.L. Fulton, D.J. Beebe, The present and future role of microfluidics in biomedical research, Nature. 507 (2014) 181–189. doi:10.1038/nature13118.
[6] T.M. Squires, S.R. Quake, Microfluidics: Fluid physics at the nanoliter scale, Reviews of Modern Physics. 77 (2005) 977–1026. doi:10.1103/RevModPhys.77.977.

[7] T. Schneider, J. Kreutz, D.T. Chiu, The Potential Impact of Droplet Microfluidics in Biology, Anal. Chem. 85 (2013) 3476–3482. doi:10.1021/ac400257c.
[8] T.M. Tran, F. Lan, C.S. Thompson, A.R. Abate, From tubes to drops: droplet-based microfluidics for ultrahigh-throughput biology, J. Phys. D: Appl. Phys. 46 (2013) 114004–22. doi:10.1088/0022-3727/46/11/114004.
[9] M.T. Guo, A. Rotem, J.A. Heyman, D.A. Weitz, Droplet microfluidics for high-throughput biological assays, Lab Chip. 12 (2012) 2146–2155 PB –. doi:10.1039/c2lc21147e.
[10] M.A. Unger, H.-P. Chou, T. Thorsen, A. Scherer, S.R. Quake, Monolithic Microfabricated Valves and Pumps by Multilayer Soft Lithography, Science. 288 (2000) 113–116. doi:10.1126/science.288.5463.113.
[11] T. Thorsen, S.J. Maerkl, S.R. Quake, Microfluidic Large-Scale Integration, Science. 298 (2002) 580–584. doi:10.1126/science.1076996.
[12] R. Gómez-Sjöberg, A.A. Leyrat, D.M. Pirone, C.S. Chen, S.R. Quake, Versatile, Fully Automated, Microfluidic Cell Culture System, Anal. Chem. 79 (2007) 8557–8563. doi:10.1021/ac071311w.
[13] Carl L Hansen, Scott Classen, A. James M Berger, Stephen R Quake, A Microfluidic Device for Kinetic Optimization of Protein Crystallization and In Situ Structure Determination, American Chemical Society, 2006. doi:10.1021/ja0576637.
[14] J. Leng, J.-B. Salmon, Microfluidic crystallization, Lab Chip. 9 (2009) 24–34. doi:10.1039/B807653G.
[15] C.L. Hansen, E. Skordalakes, J.M. Berger, S.R. Quake, A robust and scalable microfluidic metering method that allows protein crystal growth by free interface diffusion, Proceedings of the …. 99 (2002) 16531–16536. doi:10.1073/pnas.262485199.
[16] V. Lecault, A.K. White, A. Singhal, C.L. Hansen, Microfluidic single cell analysis: from promise to practice, Current Opinion in Chemical Biology. 16 (2012) 381–390. doi:10.1016/j.cbpa.2012.03.022.
[17] J.S. Marcus, W.F. Anderson, S.R. Quake, Microfluidic Single-Cell mRNA Isolation and Analysis, Anal. Chem. 78 (2006) 3084–3089. doi:10.1021/ac0519460.
[18] Y. Lu, Q. Xue, M.R. Eisele, E.S. Sulistijo, K. Brower, L. Han, et al., Highly multiplexed profiling of single-cell effector functions reveals deep functional heterogeneity in response to pathogenic ligands, Proceedings of the …. 112 (2015) E607–E615. doi:10.1073/pnas.1416756112.
[19] S.J. Maerkl, S.R. Quake, Experimental determination of the evolvability of a transcription factor, Proc. Natl. Acad. Sci. U.S.a. 106 (2009) 18650–18655. doi:10.1073/pnas.0907688106.
[20] P.M. Fordyce, D. Gerber, D. Tran, J. Zheng, H. Li, J.L. DeRisi, et al., De novo identification and biophysical characterization of transcription-factor binding sites with microfluidic affinity analysis, Nat Biotechnol. 28 (2010) 970–975. doi:10.1038/nbt.1675.
[21] A.K. White, M. VanInsberghe, O.I. Petriv, M. Hamidi, D. Sikorski, M.A. Marra, et al., High-throughput microfluidic single-cell RT-qPCR, Proceedings of the …. 108 (2011) 13999–14004. doi:10.1073/pnas.1019446108.
[22] R.E. Gerver, R. Gómez-Sjöberg, B.C. Baxter, K.S. Thorn, P.M. Fordyce, C.A. Diaz-Botia, et al., Programmable microfluidic synthesis of spectrally encoded microspheres, Lab Chip. 12 (2012) 4716–4723. doi:10.1039/C2LC40699C.
[23] H.Q. Nguyen, K. Brower, B. Harink, B. Baxter, K.S. Thorn, P.M. Fordyce, Peptide library synthesis on spectrally encoded beads for multiplexed protein/peptide bioassays, in: B.L. Gray,
H. Becker (Eds.), SPIE BiOS, SPIE, 2017: pp. 100610Z–11. doi:10.1117/12.2254908.
[24] H.Q. Nguyen, B.C. Baxter, K. Brower, C.A. Diaz-Botia, J.L. DeRisi, P.M. Fordyce, et al., Programmable Microfluidic Synthesis of Over One Thousand Uniquely Identifiable Spectral Codes, Advanced Optical Materials. (2016). doi:10.1002/adom.201600548.
[25] W.H. Grover, R.H.C. Ivester, E.C. Jensen, R.A. Mathies, Development and multiplexed control of latching pneumatic valves using microfluidic logical structures, Lab on a Chip. 6 (2006) 623–

631. doi:10.1039/B518362F.
[26] P.M. Fordyce, C.A. Diaz-Botia, J.L. DeRisi, R. Gómez-Sjöberg, Systematic characterization of feature dimensions and closing pressures for microfluidic valves produced via photoresist reflow, 12 (2012) 4287–4295. doi:10.1039/C2LC40414A.
[27] D. Marshall, Microfluidics for single cell analysis, Current Opinion in Biotechnology. 23 (2012) 109–118. doi:10.1016/j.copbio.2011.11.002.
[28] C. Hansen, Microfluidics in structural biology: smaller, faster… better, Current Opinion in Structural Biology. 13 (2003) 538–544. doi:10.1016/j.sbi.2003.09.010.
[29] M.L. Kovarik, P.C. Gach, D.M. Ornoff, Y. Wang, Micro total analysis systems for cell biology and biochemical assays, Analytical …. (2011).
[30] D.S. Kong, T.A. Thorsen, J. Babb, S.T. Wick, J.J. Gam, R. Weiss, et al., Open-source, community-driven microfluidics with Metafluidics, Nat Biotechnol. 35 (2017) 523–529. doi:10.1038/nbt.3873.
[31] E.T. da Costa, M.F. Mora, P.A. Willis, C.L. do Lago, H. Jiao, C.D. Garcia, Getting started with open-hardware: Development and control of microfluidic devices, Electrophoresis. 35 (2014) 2370–2377. doi:10.1002/elps.201400128.
[32] K. Brower, A.K. White, P.M. Fordyce, Multi-step Variable Height Photolithography for Valved Multilayer Microfluidic Devices, JoVE. (2017) 1–12. doi:10.3791/55276.
[33] R. Gómez-Sjöberg, Rafael's Microfluidics Site, (n.d.). https://sites.google.com/site/rafaelsmicrofluidicspage/valve-controllers.
[34] A.K. White, K.A. Heyries, C. Doolin, M. VanInsberghe, C.L. Hansen, High-Throughput Microfluidic Single-Cell Digital Polymerase Chain Reaction, Anal. Chem. 85 (2013) 7182– 7190. doi:10.1021/ac400896j.
[35] S.J. Maerkl, S.R. Quake, A Systems Approach to Measuring the Binding Energy Landscapes of Transcription Factors, Science. 315 (2007) 233–237. doi:10.1126/science.1131007.
[36] D.I. Walsh III, D.S. Kong, S.K. Murthy, P.A. Carr, Enabling Microfluidics: from Clean Rooms to Makerspaces, Trends in Biotechnology. 35 (2017) 383–392. doi:10.1016/j.tibtech.2017.01.001.

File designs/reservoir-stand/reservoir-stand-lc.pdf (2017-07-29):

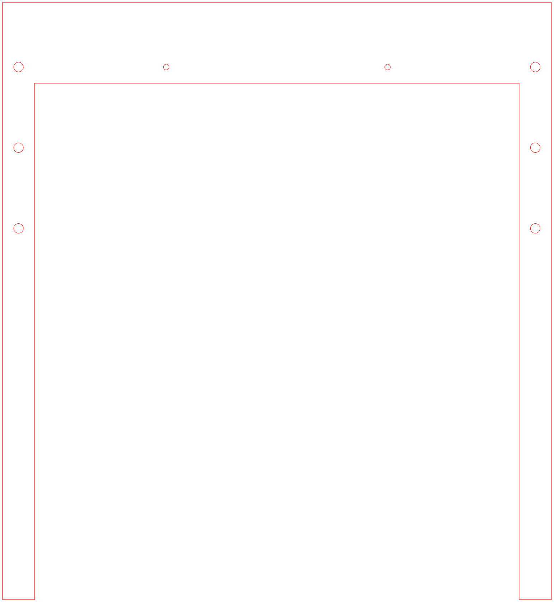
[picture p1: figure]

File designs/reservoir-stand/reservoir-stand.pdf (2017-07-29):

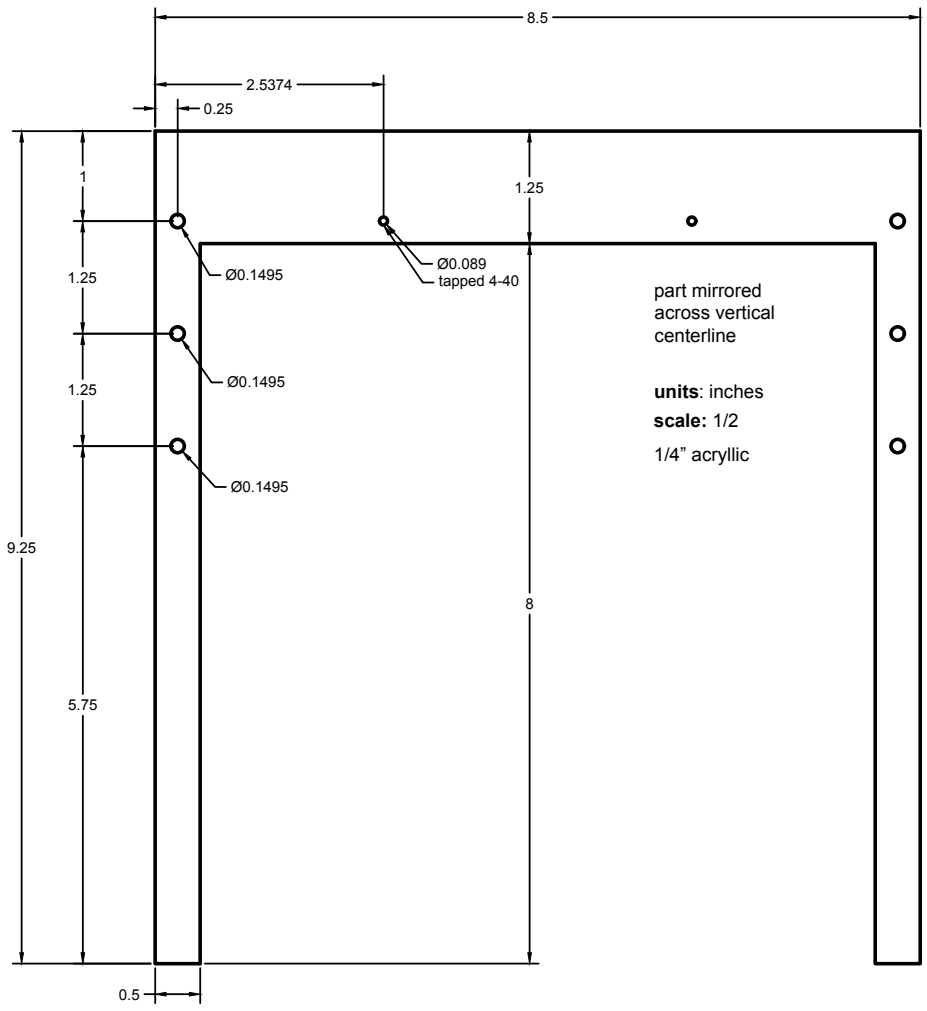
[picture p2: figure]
tapped 4-40; part mirrored across vertical centerline; units: inches; 1/4” acryllic; scale: 1/2

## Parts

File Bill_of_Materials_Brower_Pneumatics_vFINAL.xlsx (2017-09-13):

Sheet: Build Option 1 FULL BUILD
GLOBAL REQUIREMENTS BY MODULE FOR FULL BUILD (48 CONTROL LINES, 18 FLOW LINES, OPTION 1).
Table 1: Global Tubing Requirements
Component | Source | Catalog Number | Quantity | Cost Per Unit | Total Cost | Designator | Link
1/4" OD x 1/8" ID polyurethane tubing, blue, 50 ft roll | McMaster-Carr | 5648K74 | 1 | $29.00 | $29.00 | T1 | https://www.mcmaster.com/#catalog/123/136/=1773uz2
1/4" OD x 1/8" ID Tygon tubing, clear, 50 ft roll | McMaster-Carr | 6516T14 | 1 | $40.50 | $40.50 | T2 | https://www.mcmaster.com/#standard-plastic-and-rubber-tubing/=18rrbqe
5/32" OD x 3/32" ID polyurethane tubing, clear, 100 ft roll | Pneumadyne | PU-156F-0 | 1 | $17.00 | $17.00 | T3 | https://www.pneumadyne.com/532-332-polyurethane-tubing-100-p-3158.html?cPath=277_278_281
3/16" OD x 1/8" ID Tygon tubing, opaque, 50 ft roll | Grainger | 2LPR9 | 1 | $17.41 | $17.41 | T4 | https://www.grainger.com/product/TYGON-Tygon-PVC-Tubing-2LPR9
Tygon ND-100-80 Tubing (500' roll, 0.06" OD, 0.02" ID) | Fisher Scientific | 14-171-284 | 1 | $317.00 | $317.00 | T5 | https://www.fishersci.com/shop/products/saint-gobain-tygon-nd-100-80-tubing-5/14171284?searchHijack=true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
Spirally-Cut Cable Wrap, 3/8" O.D., Black Polyethylene | M.M. Newman Corp. | HT 3/8 UR-25 | 1 | $14.98 | $14.98 | T6 | https://products.mmnewman.com/heli-tube-spiral-wrap-abrasion-protector/heli-tube-spiral-cable-wrap-and-abrasion-protector/polyethylene-heli-tube-spiral-cable-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
Table 2: Pneumatic Control System, Module I: Base Board, Pressure Regulator Manifolds, and Flow Lines
Component | Source | Catalog Number | Quantity | Cost Per Unit | Total Cost | Designator | Link
Double Standard Solid 80/20 Rails (26" x 2" x 1") | McMaster-Carr | 47065T803 | 2 | $21.06 | $42.12 | b1 | https://www.mcmaster.com/#80/20-compatible-t-slotted-framing/=16fvjvl
Single Standard Solid 80/20 Rails (26" x 1" x 1") | McMaster-Carr | 47065T848 | 3 | $9.36 | $28.08 | b2 | https://www.mcmaster.com/#80/20-compatible-t-slotted-framing/=18ra8pu
Double Standard Hollow 80/20 Rails (12" x 2" x 1") | McMaster-Carr | 47065T107 | 2 | $9.13 | $18.26 | b3 | https://www.mcmaster.com/#80/20-compatible-t-slotted-framing/=16fvjvl
Diagonal 80/20 Rail (6" x 1" x 1") | McMaster-Carr | 47065T186 | 2 | $15.67 | $31.34 | b4 | https://www.mcmaster.com/#80/20-compatible-t-slotted-framing/=16fvpjy
Standard End Feed Fasteners, Pack of 4 | McMaster-Carr | 47065T142 | 6 | $2.30 | $13.80 | b5 | https://www.mcmaster.com/#80/20-compatible-t-slotted-framing/=16fvqsz
Elbow Bracket 4-Hole Extended Corner Bracket | McMaster-Carr | 47065T239 | 8 | $5.85 | $46.80 | b6 | https://www.mcmaster.com/#80/20-compatible-t-slotted-framing/=16fvqsz
Extended Corner 8-Hole Fastener | McMaster-Carr | 47065T253 | 2 | $8.79 | $17.58 | b7 | https://www.mcmaster.com/#80/20-compatible-t-slotted-framing/=16fvqsz
Corner 5-Hole Surface Bracket | McMaster-Carr | 47065T267 | 2 | $8.47 | $16.94 | b8 | https://www.mcmaster.com/#80/20-compatible-t-slotted-framing/=16fvqsz
10-32 1/2" Socket Head Screws, Pack of 100 | McMaster-Carr | 91251A342 | 1 | $9.60 | $9.60 | s1 | https://www.mcmaster.com/#standard-socket-head-screws/=17noq20
6/32 1-1/2" Partially-Threaded Socket Head Screws, Pack of 50 | McMaster-Carr | 91251A157 | 1 | $9.94 | $9.94 | s2 | https://www.mcmaster.com/#standard-socket-head-screws/=17noq20
6-32 1/4" Socket Head Screws, Pack of 100 | McMaster-Carr | 91251A144 | 1 | $8.46 | $8.46 | s3 | https://www.mcmaster.com/#standard-socket-head-screws/=17noq20
SMC Precision Air Regulator, 1/4" ports, 60 psi upper range | Stevens Engineering | IR2010-N02 | 3 | $75.80 | $227.40 | A | http://www.smcpneumatics.com/IR2010-N02.html
Pressure Gauge, 1/4" Back Connector, 0-60 psi | McMaster-Carr | 4000K791 | 3 | $12.03 | $36.09 | B | https://www.mcmaster.com/#catalog/123/594/=16cczr8
1/4" NPT to 1/4" Brass Push-to-Connect Tube Fitting | McMaster-Carr | 7880T125 | 16 | $2.24 | $35.84 | C | https://www.mcmaster.com/#catalog/123/208/=16cd5qx
Brass Tee Fitting, 1/4" NPT, FxFxM | McMaster-Carr | 50785K222 | 6 | $4.90 | $29.40 | D | https://www.mcmaster.com/#catalog/123/36/=16cdg0i
Brass Elbow Fitting, 1/4" NPT, FxM | McMaster-Carr | 50785K43 | 6 | $2.50 | $15.00 | E | https://www.mcmaster.com/#catalog/123/36/=16cdm54
Precision Air Regulator, 1/4" ports, 30 psi lower range | Stevens Engineering | IR2000-O2-A | 3 | $75.80 | $227.40 | F | http://www.smcpneumatics.com/IR2000-02-A.html
Digital Pressure Gauge, 1/4" MNPT, 0-30 psi | McMaster-Carr | 3943K15 | 3 | $428.45 | $1285.35 | G | https://www.mcmaster.com/#catalog/123/606/=16cdr7o
Male Luer Integral Lock Ring, 400 series, 1/8" barb, Pack of 100 | Value Plastics | MTLL430-9002 | 1 | $20.20 | $20.20 | H | https://www.nordsonmedical.com/search/search.aspx?s=MTLL430-9002
1-Way Luer Stopcock, M Lock, Pack of 100 | Cole-Parmer | Sk-30600-05 | 1 | $185.00 | $185.00 | I | https://www.coleparmer.com/i/cole-parmer-stopcocks-with-luer-connection-male-lock-1-way-100-pack-non-sterile/3060005?searchterm=30600-05
Female Luer 1/4"-28 Panel Mount to 1/8" Barb, Pack of 100 | Value Plastics | FTLLB230-1 | 1 | $19.00 | $19.00 | J | http://www.nordsonmedical.com/search/search.aspx?s=FTLLB230-1
Tee Tube Fitting for 1/8" ID Tubing, Pack of 100 | Value Plastics | T230-1 | 1 | $26.80 | $26.80 | K | https://www.nordsonmedical.com/search/search.aspx?s=T230-1
Luer Plug Caps, Pack of 10 | McMaster-Carr | 51525K311 | 1 | $2.41 | $2.41 | L | https://www.mcmaster.com/#catalog/123/227/=16ecdqs
Male Luer Integral Lock Ring, 1/8" barb, Pack of 100 | Value Plastics | MTLL230-9 | 1 | $20.20 | $20.20 | M | https://www.nordsonmedical.com/search/search.aspx?s=MTLL230-9
4-Way Luer Stopcock, M Lock, F Connectors, Pack of 100 | Cole-Parmer | EW-30600-09 | 1 | $185.00 | $185.00 | N | https://www.coleparmer.com/i/cole-parmer-stopcocks-with-luer-connections-4-way-male-lock-100-pack-non-sterile/3060009?searchterm=EW-30600-09
Blunt Stainless Steel Luer Lock Needle, Pack of 50 | McMaster-Carr | 75165A684 | 1 | $11.88 | $11.88 | O | https://www.mcmaster.com/#catalog/123/3482/=16cdrw6
4 -Station Control Manifold, 1/4" NPT-F inlets, 1/8" NPT outlets | Pneumadyne | M10-125-4 | 2 | $12.60 | $25.20 | P | https://www.pneumadyne.com/station-npt-input-aluminum-manifold-p-2577.html
Dented Toggle Control Switch, 1/8" NPT input, 10/32" output | Pneumadyne | C030621 | 8 | $14.06 | $112.48 | Q | https://www.pneumadyne.com/detented-toggle-control-valves-p-302.html?cPath=2_19_22
10-32 UNF to 1/4" Push-to-Connect Tube Fitting | McMaster-Carr | 7880T122 | 8 | $3.31 | $26.48 | R | https://www.mcmaster.com/#7880t122/=16cdbih
1/4" Push-to-Connect Plug | McMaster-Carr | 5779K54 | 2 | $1.16 | $2.32 | S | https://www.mcmaster.com/#catalog/123/200/=16cdead
Table 3: Pneumatic Control System, Module 2: Filter Assembly to House Air
Component | Source | Catalog Number | Quantity | Cost Per Unit | Total Cost | Designator | Link
3-Way 1/4" Push-to-Connect Manifold | McMaster-Carr | 5779K318 | 2 | $16.60 | $33.20 | T | https://www.mcmaster.com/#catalog/123/200/=16ecvas
1/4" NPT to 1/4" Brass Push-to-Connect Tube Fitting | McMaster-Carr | 7880T125 | 2 | $2.24 | $4.48 | C | https://www.mcmaster.com/#catalog/123/208/=16cd5qx
Brass Ball Valve, T-handle, 1/4" NPT FxM | McMaster-Carr | 4912K92 | 1 | $7.02 | $7.02 | U | https://www.mcmaster.com/#catalog/123/454/=16ed8yv
Wilkerson Modular Compressed Air Filter, 5 um, 1/4" Connector | McMaster-Carr | 60115K19 | 1 | $70.27 | $70.27 | V | https://www.mcmaster.com/#catalog/123/1028/=16ed4s0
Filter Joiner Clamp | McMaster-Carr | 60115K22 | 1 | $13.05 | $13.05 | X | https://www.mcmaster.com/#catalog/123/1028/=16ed4s0
Standard Oil vapor and Odor Removal Filter, 0.003 um | McMaster-Carr | 7426K11 | 1 | $80.10 | $80.10 | Y | https://www.mcmaster.com/#catalog/123/1028/=16ed4s0
Brass Elbow Fitting, 1/4" NPT, FxM | McMaster-Carr | 50785K43 | 1 | $2.50 | $2.50 | E | https://www.mcmaster.com/#catalog/123/36/=16cdm54
1/4" Push-to-Connect Plug | McMaster-Carr | 5779K54 | 1 | $1.16 | $1.16 | S | https://www.mcmaster.com/#catalog/123/200/=16cdead
Table 4: Pneumatic Control System, Module 3: Control 8-Valve Solenoid Manifolds
Component | Source | Catalog Number | Quantity | Cost Per Unit | Total Cost | Designator | Link
4-Way Luer Stopcock, M Lock, F Connectors, Pack of 100 | Cole-Parmer | EW-30600-09 | 0 | $185.00 | $0.00 | N | https://www.coleparmer.com/i/cole-parmer-stopcocks-with-luer-connections-4-way-male-lock-100-pack-non-sterile/3060009?searchterm=EW-30600-09
10-32" Special Tapered Thread to Male Luer w 1/4" Hex, Pack of 100 | Value Plastics | XMLRL-9 | 1 | $34.80 | $34.80 | a | http://www.nordsonmedical.com/search/search.aspx?s=XMLRL-9
Finger Snap Luer Lock Ring, Pack of 100 | Value Plastics | FSLLR-9002 | 1 | $14.50 | $14.50 | b | http://www.nordsonmedical.com/search/search.aspx?s=FSLLR-9002
Male Luer to Barb Elbow, 1/8" ID Tubing, Pack of 100 | Value Plastics | LE7230-9 | 1 | $50.40 | $50.40 | c | http://www.nordsonmedical.com/search/search.aspx?s=LE7230-9
Luer Adapter, Pair to Female 1/4"-28 | Idex | P-628 | 48 | $3.90 | $187.20 | d | https://www.idex-hs.com/luer-adapter-female-luer-female-union.html?optionvalue=4751
Flangeless Ferrule (ETFE), 1/4"-28 Flat-Bottom, Pack of 25 | Idex | P200 | 2 | $32.75 | $65.50 | e | https://www.idex-hs.com/flangeless-ferrule-tefzelr-etfe-1-4-28-flat-bottom-for-1-16-od.html
Flangeless Male Nut, 1/4"-28 Flat-Bottom, 1/16" OD Red, Pack of 25 | Idex | P202 | 2 | $32.75 | $65.50 | f | https://www.idex-hs.com/flangeless-male-nut-delrinr-1-4-28-flat-bottom-1-16-od.html
1/4" to 5/32" NPTF-M Push-to-Connect | McMaster-Carr | 51055K8 | 48 | $1.99 | $95.52 | g | https://www.mcmaster.com/#catalog/123/216/=16ec31e
Luer Plug Caps, Pack of 10 | McMaster-Carr | 51525K311 | 0 | $2.41 | $0.00 | L | https://www.mcmaster.com/#catalog/123/227/=16ecdqs
Steel Blunt Pins, 1/2" length, Pack of 250 | New England Small Tube | NE-1310-02 | 1 | $212.50 | $212.50 | P1 | http://www.nesmalltube.com
Tee Tube Fitting for 1/8" ID Tubing, Pack of 100 | Value Plastics | T230-1 | 0 | $26.80 | $0.00 | K | https://www.nordsonmedical.com/search/search.aspx?s=T230-1
8-Valve Solenoid Valve Manifold | Festo | MH1A24VDCNHC8VPRK01QMAPBPCXDX | 6 | $564.71 | $3388.26 | h | https://www.festo.com/cat/en-us_us/products_MH?CurrentPartNo=197334
Table 5: Pneumatic Control System, Module 4: Control Loading
Component | Source | Catalog Number | Quantity | Cost Per Unit | Total Cost | Designator | Link
Male Luer Integral Lock Ring, 1/8" barb, Pack of 100 | Value Plastics | MTLL230-9 | 0 | $20.20 | $0.00 | M | https://www.nordsonmedical.com/search/search.aspx?s=MTLL230-9
Female Luer 1/4"-28 Panel Mount to 1/8" Barb, Pack of 100 | Value Plastics | FTLLB230-1 | 0 | $19.00 | $0.00 | J | http://www.nordsonmedical.com/search/search.aspx?s=FTLLB230-1
Nylon 1/4"-28 Hex Nut, Pack of 100 | McMaster-Carr | 94812A800 | 1 | $6.47 | $6.47 | i | https://www.mcmaster.com/#catalog/123/3212/=16edwvq
Scientific Nalgene Polypropelene Wide Mouth Bottle | Cole-Parmer | EW-06057-10 | 1 | $26.36 | $26.36 | j | https://www.coleparmer.com/i/thermo-scientific-nalgene-2121-0005-polypropylene-wide-mouth-bottle-2-l/0605710
Luer Lock Manifold, 5 Ports, F Luer, Pack of 10 | Cole-Parmer | EW-30600-43 | 1 | $95.00 | $95.00 | k | https://www.coleparmer.com/i/cole-parmer-manifolds-with-luer-locks-5-ports-360-rotation-10-pack-non-sterile/3060043
1-Way Luer Stopcock, M Lock, Pack of 100 | Cole-Parmer | Sk-30600-05 | 0 | $185.00 | $0.00 | I | https://www.coleparmer.com/i/cole-parmer-stopcocks-with-luer-connection-male-lock-1-way-100-pack-non-sterile/3060005?searchterm=30600-05
Male Luer Integral Lock Ring, 1/8" barb, Pack of 100 | Value Plastics | MTLL430-9002 | 0 | $20.20 | $0.00 | H | https://www.nordsonmedical.com/search/search.aspx?s=MTLL430-9002
Table 6: Digital Modbus Control
Component | Source | Catalog Number | Quantity | Cost Per Unit | Total Cost | Designator | Link | Material Type
WAGO Programmable I/O Controller | WAGO | 750-881 | 1 | $665.00 | $665.00 | W1 | http://www.wago.us/products/components-for-automation/modular-io-system-series-750-753/programmable-fieldbus-controller/ethernet/index-2.jsp
WAGO AC/DC DIN Rail Power Supply, 240W | WAGO | 787-732 | 1 | $135.00 | $135.00 | W2 | https://eshop.wago.com/JPBC/0_5StartPage.jsp?supplierAID=787-732&catalogID=WAGO01&zone=7
WAGO 4-channel digital output, 24 V, 0.5 A | WAGO | 750-504 | 14 | $72.22 | $1011.08 | W3 | https://eshop.wago.com/JPBC/0_5StartPage.jsp?supplierAID=750-504&catalogID=WAGO01&zone=7
WAGO I/O End Module | WAGO | 750-600 | 1 | $20.00 | $20.00 | W5 | https://eshop.wago.com/JPBC/0_5StartPage.jsp?supplierAID=750-600&catalogID=WAGO01&zone=7
Mounting Rail, DIN 3 Rail, 35 mm wide, 1 m long | McMaster-Carr | 8961K15 | 1 | $5.07 | $5.07 | W6 | https://www.mcmaster.com/#catalog/122/777/=15kgz5u
Ethernet Cable , CAT5E | Digikey | AE10492-ND | 1 | $4.66 | $4.66 | m | http://www.digikey.com/products/en?keywords=AE10492-ND
8 ft. Power Cord with SPT-1 NEC Cord | Grainger | 1FD95 | 1 | $7.76 | $7.76 | n | https://www.grainger.com/product/POWER-FIRST-Powersupply-Cord-1FD95?cm_mmc=EMT-_-ShipConfirm-_-SAPShipConfirm-_-sku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
Assorted Wire, Red and Black, 18G | Amazon | SW18A08F5C2 | 1 | $5.98 | $5.98 | o | https://www.amazon.com/dp/B01CL3M7A4?psc=1
Table 7: Machined, Cut, and Printing Cost Estimates
Baseboard (backboard, laser cut acrylic) | Laser Cut, TAP Plastics |  | 1 | $110.77 | $110.77 | - | Quotes are included on the Github respository, https://github.com/FordyceLab/Open_Source_Pneumatics
Flow Control Manifolds (stopcock-mount, 3D printed ABS) | 3D Printed, uPrint |  | 6 | $12.00 | $72.00 | -
Water Reservoir Stand (reservoir-stand, laser cut acrylic) | Laser Cut, Big Blue Saw |  | 6 | $14.38 | $86.28 | -
Control Water Reservoir (reservoir, machined acrylic) | Machined |  | 6 | $105.00 | $630.00 | -
Note: Counts of 0 mean that that part has been purchased previously in large enough quantities by a previous build module.
 |  | OPTION 1 FULL BUILD |  | TOTAL COST | $10379.65

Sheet: Build Option 2 ABRIDGED BUILD
GLOBAL REQUIREMENTS BY MODULE FOR ABRIDGED BUILD (8 CONTROL LINES, 6 FLOW LINES, OPTION 2).
Table 1: Global Tubing Requirements
Component | Source | Catalog Number | Quantity | Cost Per Unit | Total Cost | Designator | Link
1/4" OD x 1/8" ID polyurethane tubing, blue, 50 ft roll | McMaster-Carr | 5648K74 | 1 | $29.00 | $29.00 | T1 | https://www.mcmaster.com/#catalog/123/136/=1773uz2
1/4" OD x 1/8" ID Tygon tubing, clear, 50 ft roll | McMaster-Carr | 6516T14 | 1 | $40.50 | $40.50 | T2 | https://www.mcmaster.com/#standard-plastic-and-rubber-tubing/=18rrbqe
5/32" OD x 3/32" ID polyurethane tubing, clear, 100 ft roll | Pneumadyne | PU-156F-0 | 1 | $17.00 | $17.00 | T3 | https://www.pneumadyne.com/532-332-polyurethane-tubing-100-p-3158.html?cPath=277_278_281
3/16" OD x 1/8" ID Tygon tubing, opaque, 50 ft roll | Grainger | 2LPR9 | 1 | $17.41 | $17.41 | T4 | https://www.grainger.com/product/TYGON-Tygon-PVC-Tubing-2LPR9
Tygon ND-100-80 Tubing (500' roll, 0.06" OD, 0.02" ID) | Fisher Scientific | 14-171-284 | 1 | $317.00 | $317.00 | T5 | https://www.fishersci.com/shop/products/saint-gobain-tygon-nd-100-80-tubing-5/14171284?searchHijack=true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
Spirally-Cut Cable Wrap, 3/8" O.D., Black Polyethylene | M.M. Newman Corp. | HT 3/8 UR-25 | 1 | $14.98 | $14.98 | T6 | https://products.mmnewman.com/heli-tube-spiral-wrap-abrasion-protector/heli-tube-spiral-cable-wrap-and-abrasion-protector/polyethylene-heli-tube-spiral-cable-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
Table 2: Pneumatic Control System, Module I: Base Board, Pressure Regulator Manifolds, and Flow Lines
Component | Source | Catalog Number | Quantity | Cost Per Unit | Total Cost | Designator | Link
Double Standard Solid 80/20 Rails (26" x 2" x 1") | McMaster-Carr | 47065T803 | 2 | $21.06 | $42.12 | b1 | https://www.mcmaster.com/#80/20-compatible-t-slotted-framing/=16fvjvl
Single Standard Solid 80/20 Rails (26" x 1" x 1") | McMaster-Carr | 47065T848 | 3 | $9.36 | $28.08 | b2 | https://www.mcmaster.com/#80/20-compatible-t-slotted-framing/=18ra8pu
Double Standard Hollow 80/20 Rails (12" x 2" x 1") | McMaster-Carr | 47065T107 | 2 | $9.13 | $18.26 | b3 | https://www.mcmaster.com/#80/20-compatible-t-slotted-framing/=16fvjvl
Diagonal 80/20 Rail (6" x 1" x 1") | McMaster-Carr | 47065T186 | 2 | $15.67 | $31.34 | b4 | https://www.mcmaster.com/#80/20-compatible-t-slotted-framing/=16fvpjy
Standard End Feed Fasteners, Pack of 4 | McMaster-Carr | 47065T142 | 6 | $2.30 | $13.80 | b5 | https://www.mcmaster.com/#80/20-compatible-t-slotted-framing/=16fvqsz
Elbow Bracket 4-Hole Extended Corner Bracket | McMaster-Carr | 47065T239 | 3 | $5.85 | $17.55 | b6 | https://www.mcmaster.com/#80/20-compatible-t-slotted-framing/=16fvqsz
Extended Corner 8-Hole Fastener | McMaster-Carr | 47065T253 | 2 | $8.79 | $17.58 | b7 | https://www.mcmaster.com/#80/20-compatible-t-slotted-framing/=16fvqsz
Corner 5-Hole Surface Bracket | McMaster-Carr | 47065T267 | 2 | $8.47 | $16.94 | b8 | https://www.mcmaster.com/#80/20-compatible-t-slotted-framing/=16fvqsz
10-32 1/2" Socket Head Screws, Pack of 100 | McMaster-Carr | 91251A342 | 1 | $9.60 | $9.60 | s1 | https://www.mcmaster.com/#standard-socket-head-screws/=17noq20
6/32 1-1/2" Partially-Threaded Socket Head Screws, Pack of 50 | McMaster-Carr | 91251A157 | 1 | $9.94 | $9.94 | s2 | https://www.mcmaster.com/#standard-socket-head-screws/=17noq20
6-32 1/4" Socket Head Screws, Pack of 100 | McMaster-Carr | 91251A144 | 1 | $8.46 | $8.46 | s3 | https://www.mcmaster.com/#standard-socket-head-screws/=17noq20
SMC Precision Air Regulator, 1/4" ports, 60 psi upper range | Stevens Engineering | IR2010-N02 | 2 | $75.80 | $151.60 | A | http://www.smcpneumatics.com/IR2010-N02.html
Pressure Gauge, 1/4" Back Connector, 0-60 psi | McMaster-Carr | 4000K791 | 2 | $12.03 | $24.06 | B | https://www.mcmaster.com/#catalog/123/594/=16cczr8
1/4" NPT to 1/4" Brass Push-to-Connect Tube Fitting | McMaster-Carr | 7880T125 | 8 | $2.24 | $17.92 | C | https://www.mcmaster.com/#catalog/123/208/=16cd5qx
Brass Tee Fitting, 1/4" NPT, FxFxM | McMaster-Carr | 50785K222 | 3 | $4.90 | $14.70 | D | https://www.mcmaster.com/#catalog/123/36/=16cdg0i
Brass Elbow Fitting, 1/4" NPT, FxM | McMaster-Carr | 50785K43 | 3 | $2.50 | $7.50 | E | https://www.mcmaster.com/#catalog/123/36/=16cdm54
Precision Air Regulator, 1/4" ports, 30 psi lower range | Stevens Engineering | IR2000-O2-A | 1 | $75.80 | $75.80 | F | http://www.smcpneumatics.com/IR2000-02-A.html
Digital Pressure Gauge, 1/4" MNPT, 0-30 psi | McMaster-Carr | 3943K15 | 1 | $428.45 | $428.45 | G | https://www.mcmaster.com/#catalog/123/606/=16cdr7o
Male Luer Integral Lock Ring, 400 series, 1/8" barb, Pack of 100 | Value Plastics | MTLL430-9002 | 1 | $20.20 | $20.20 | H | https://www.nordsonmedical.com/search/search.aspx?s=MTLL430-9002
1-Way Luer Stopcock, M Lock, Pack of 100 | Cole-Parmer | Sk-30600-05 | 1 | $185.00 | $185.00 | I | https://www.coleparmer.com/i/cole-parmer-stopcocks-with-luer-connection-male-lock-1-way-100-pack-non-sterile/3060005?searchterm=30600-05
Female Luer 1/4"-28 Panel Mount to 1/8" Barb, Pack of 100 | Value Plastics | FTLLB230-1 | 1 | $19.00 | $19.00 | J | http://www.nordsonmedical.com/search/search.aspx?s=FTLLB230-1
Tee Tube Fitting for 1/8" ID Tubing, Pack of 100 | Value Plastics | T230-1 | 1 | $26.80 | $26.80 | K | https://www.nordsonmedical.com/search/search.aspx?s=T230-1
Luer Plug Caps, Pack of 10 | McMaster-Carr | 51525K311 | 1 | $2.41 | $2.41 | L | https://www.mcmaster.com/#catalog/123/227/=16ecdqs
Male Luer Integral Lock Ring, 1/8" barb, Pack of 100 | Value Plastics | MTLL230-9 | 1 | $20.20 | $20.20 | M | https://www.nordsonmedical.com/search/search.aspx?s=MTLL230-9
4-Way Luer Stopcock, M Lock, F Connectors, Pack of 100 | Cole-Parmer | EW-30600-09 | 1 | $185.00 | $185.00 | N | https://www.coleparmer.com/i/cole-parmer-stopcocks-with-luer-connections-4-way-male-lock-100-pack-non-sterile/3060009?searchterm=EW-30600-09
Blunt Stainless Steel Luer Lock Needle, Pack of 50 | McMaster-Carr | 75165A684 | 1 | $11.88 | $11.88 | O | https://www.mcmaster.com/#catalog/123/3482/=16cdrw6
4 -Station Control Manifold, 1/4" NPT-F inlets, 1/8" NPT outlets | Pneumadyne | M10-125-4 | 1 | $12.60 | $12.60 | P | https://www.pneumadyne.com/station-npt-input-aluminum-manifold-p-2577.html
Dented Toggle Control Switch, 1/8" NPT input, 10/32" output | Pneumadyne | C030621 | 4 | $14.06 | $56.24 | Q | https://www.pneumadyne.com/detented-toggle-control-valves-p-302.html?cPath=2_19_22
10-32 UNF to 1/4" Push-to-Connect Tube Fitting | McMaster-Carr | 7880T122 | 4 | $3.31 | $13.24 | R | https://www.mcmaster.com/#7880t122/=16cdbih
1/4" Push-to-Connect Plug | McMaster-Carr | 5779K54 | 1 | $1.16 | $1.16 | S | https://www.mcmaster.com/#catalog/123/200/=16cdead
Table 3: Pneumatic Control System, Module 2: Filter Assembly to House Air
Component | Source | Catalog Number | Quantity | Cost Per Unit | Total Cost | Designator | Link
3-Way 1/4" Push-to-Connect Manifold | McMaster-Carr | 5779K318 | 1 | $16.60 | $16.60 | T | https://www.mcmaster.com/#catalog/123/200/=16ecvas
1/4" NPT to 1/4" Brass Push-to-Connect Tube Fitting | McMaster-Carr | 7880T125 | 2 | $2.24 | $4.48 | C | https://www.mcmaster.com/#catalog/123/208/=16cd5qx
Brass Ball Valve, T-handle, 1/4" NPT FxM | McMaster-Carr | 4912K92 | 1 | $7.02 | $7.02 | U | https://www.mcmaster.com/#catalog/123/454/=16ed8yv
Wilkerson Modular Compressed Air Filter, 5 um, 1/4" Connector | McMaster-Carr | 60115K19 | 1 | $70.27 | $70.27 | V | https://www.mcmaster.com/#catalog/123/1028/=16ed4s0
Filter Joiner Clamp | McMaster-Carr | 60115K22 | 1 | $13.05 | $13.05 | X | https://www.mcmaster.com/#catalog/123/1028/=16ed4s0
Standard Oil vapor and Odor Removal Filter, 0.003 um | McMaster-Carr | 7426K11 | 1 | $80.10 | $80.10 | Y | https://www.mcmaster.com/#catalog/123/1028/=16ed4s0
Brass Elbow Fitting, 1/4" NPT, FxM | McMaster-Carr | 50785K43 | 1 | $2.50 | $2.50 | E | https://www.mcmaster.com/#catalog/123/36/=16cdm54
1/4" Push-to-Connect Plug | McMaster-Carr | 5779K54 | 1 | $1.16 | $1.16 | S | https://www.mcmaster.com/#catalog/123/200/=16cdead
Table 4: Pneumatic Control System, Module 3: Control 8-Valve Solenoid Manifolds
Component | Source | Catalog Number | Quantity | Cost Per Unit | Total Cost | Designator | Link
4-Way Luer Stopcock, M Lock, F Connectors, Pack of 100 | Cole-Parmer | EW-30600-09 | 0 | $185.00 | $0.00 | N | https://www.coleparmer.com/i/cole-parmer-stopcocks-with-luer-connections-4-way-male-lock-100-pack-non-sterile/3060009?searchterm=EW-30600-09
10-32" Special Tapered Thread to Male Luer w 1/4" Hex, Pack of 100 | Value Plastics | XMLRL-9 | 1 | $34.80 | $34.80 | a | http://www.nordsonmedical.com/search/search.aspx?s=XMLRL-9
Finger Snap Luer Lock Ring, Pack of 100 | Value Plastics | FSLLR-9002 | 1 | $14.50 | $14.50 | b | http://www.nordsonmedical.com/search/search.aspx?s=FSLLR-9002
Male Luer to Barb Elbow, 1/8" ID Tubing, Pack of 100 | Value Plastics | LE7230-9 | 1 | $50.40 | $50.40 | c | http://www.nordsonmedical.com/search/search.aspx?s=LE7230-9
Luer Adapter, Pair to Female 1/4"-28 | Idex | P-628 | 8 | $3.90 | $31.20 | d | https://www.idex-hs.com/luer-adapter-female-luer-female-union.html?optionvalue=4751
Flangeless Ferrule (ETFE), 1/4"-28 Flat-Bottom, Pack of 25 | Idex | P200 | 1 | $32.75 | $32.75 | e | https://www.idex-hs.com/flangeless-ferrule-tefzelr-etfe-1-4-28-flat-bottom-for-1-16-od.html
Flangeless Male Nut, 1/4"-28 Flat-Bottom, 1/16" OD Red, Pack of 25 | Idex | P202 | 1 | $32.75 | $32.75 | f | https://www.idex-hs.com/flangeless-male-nut-delrinr-1-4-28-flat-bottom-1-16-od.html
1/4" to 5/32" NPTF-M Push-to-Connect | McMaster-Carr | 51055K8 | 8 | $1.99 | $15.92 | g | https://www.mcmaster.com/#catalog/123/216/=16ec31e
Luer Plug Caps, Pack of 10 | McMaster-Carr | 51525K311 | 0 | $2.41 | $0.00 | L | https://www.mcmaster.com/#catalog/123/227/=16ecdqs
Steel Blunt Pins, 1/2" length, Pack of 250 | New England Small Tube | NE-1310-02 | 1 | $212.50 | $212.50 | P1 | http://www.nesmalltube.com
Tee Tube Fitting for 1/8" ID Tubing, Pack of 100 | Value Plastics | T230-1 | 0 | $26.80 | $0.00 | K | https://www.nordsonmedical.com/search/search.aspx?s=T230-1
8-Valve Solenoid Valve Manifold | Festo | MH1A24VDCNHC8VPRK01QMAPBPCXDX | 1 | $564.71 | $564.71 | h | https://www.festo.com/cat/en-us_us/products_MH?CurrentPartNo=197334
Table 5: Pneumatic Control System, Module 4: Control Loading
Component | Source | Catalog Number | Quantity | Cost Per Unit | Total Cost | Designator | Link
Male Luer Integral Lock Ring, 1/8" barb, Pack of 100 | Value Plastics | MTLL230-9 | 0 | $20.20 | $0.00 | M | https://www.nordsonmedical.com/search/search.aspx?s=MTLL230-9
Female Luer 1/4"-28 Panel Mount to 1/8" Barb, Pack of 100 | Value Plastics | FTLLB230-1 | 0 | $19.00 | $0.00 | J | http://www.nordsonmedical.com/search/search.aspx?s=FTLLB230-1
Nylon 1/4"-28 Hex Nut, Pack of 100 | McMaster-Carr | 94812A800 | 1 | $6.47 | $6.47 | i | https://www.mcmaster.com/#catalog/123/3212/=16edwvq
Scientific Nalgene Polypropelene Wide Mouth Bottle | Cole-Parmer | EW-06057-10 | 1 | $26.36 | $26.36 | j | https://www.coleparmer.com/i/thermo-scientific-nalgene-2121-0005-polypropylene-wide-mouth-bottle-2-l/0605710
1-Way Luer Stopcock, M Lock, Pack of 100 | Cole-Parmer | Sk-30600-05 | 0 | $185.00 | $0.00 | I | https://www.coleparmer.com/i/cole-parmer-stopcocks-with-luer-connection-male-lock-1-way-100-pack-non-sterile/3060005?searchterm=30600-05
Male Luer Integral Lock Ring, 1/8" barb, Pack of 100 | Value Plastics | MTLL430-9002 | 0 | $20.20 | $0.00 | H | https://www.nordsonmedical.com/search/search.aspx?s=MTLL430-9002
Table 6: Digital Modbus Control
Component | Source | Catalog Number | Quantity | Cost Per Unit | Total Cost | Designator | Link
WAGO Programmable I/O Controller | WAGO | 750-881 | 1 | $665.00 | $665.00 | W1 | http://www.wago.us/products/components-for-automation/modular-io-system-series-750-753/programmable-fieldbus-controller/ethernet/index-2.jsp
WAGO AC/DC DIN Rail Power Supply, 240W | WAGO | 787-732 | 1 | $135.00 | $135.00 | W2 | https://eshop.wago.com/JPBC/0_5StartPage.jsp?supplierAID=787-732&catalogID=WAGO01&zone=7
WAGO 4-channel digital output, 24 V, 0.5 A | WAGO | 750-504 | 3 | $72.22 | $216.66 | W3 | https://eshop.wago.com/JPBC/0_5StartPage.jsp?supplierAID=750-504&catalogID=WAGO01&zone=7
WAGO I/O End Module | WAGO | 750-600 | 1 | $20.00 | $20.00 | W5 | https://eshop.wago.com/JPBC/0_5StartPage.jsp?supplierAID=750-600&catalogID=WAGO01&zone=7
Mounting Rail, DIN 3 Rail, 35 mm wide, 1 m long | McMaster-Carr | 8961K15 | 1 | $5.07 | $5.07 | W6 | https://www.mcmaster.com/#catalog/122/777/=15kgz5u
Ethernet Cable , CAT5E | Digikey | AE10492-ND | 1 | $4.66 | $4.66 | m | http://www.digikey.com/products/en?keywords=AE10492-ND
8 ft. Power Cord with SPT-1 NEC Cord | Grainger | 1FD95 | 1 | $7.76 | $7.76 | n | https://www.grainger.com/product/POWER-FIRST-Powersupply-Cord-1FD95?cm_mmc=EMT-_-ShipConfirm-_-SAPShipConfirm-_-sku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
Assorted Wire, Red and Black, 18G | Amazon | SW18A08F5C2 | 1 | $5.98 | $5.98 | o | https://www.amazon.com/dp/B01CL3M7A4?psc=1
Table 7: Machined, Cut, and Printing Cost Estimates
Baseboard (backboard, laser cut acrylic) | Laser Cut, TAP Plastics |  | 1 | $110.77 | $110.77 | - | Quotes are included on the Github respository, https://github.com/FordyceLab/Open_Source_Pneumatics
Flow Control Manifolds (stopcock-mount, 3D printed ABS) | 3D Printed, uPrint |  | 2 | $12.00 | $24.00 | -
Water Reservoir Stand (reservoir-stand, laser cut acrylic) | Laser Cut, Big Blue Saw |  | 1 | $14.38 | $14.38 | -
Control Water Reservoir (reservoir, machined acrylic) | Machined |  | 1 | $105.00 | $105.00 | -
Note: Counts of 0 mean that that part has been purchased previously in large enough quantities by a previous build module.
 |  | OPTION 2 ABRIDGED BUILD |  | TOTAL COST | $4455.14
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

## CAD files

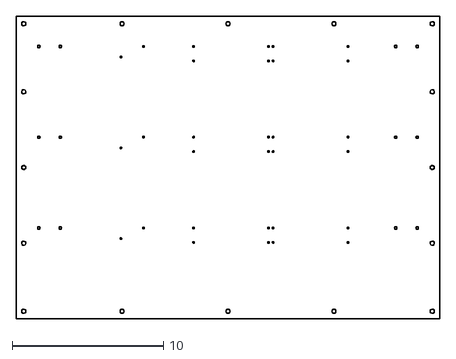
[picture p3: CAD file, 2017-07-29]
designs/backboard/backboard_full.dxf
28.0 x 20.0

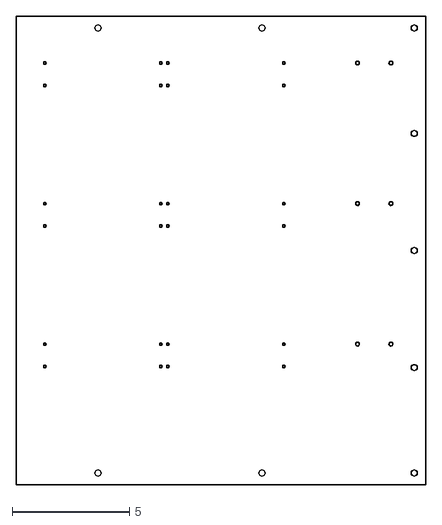
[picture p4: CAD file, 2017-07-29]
designs/backboard/backboard_right.dxf
17.5 x 20.0

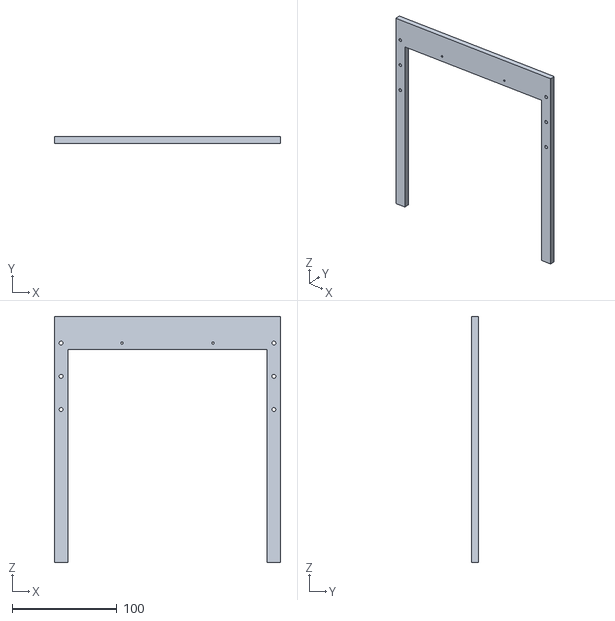
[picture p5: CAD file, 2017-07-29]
designs/reservoir-stand/reservoir-stand.stl
215.9 x 6.35 x 234.9

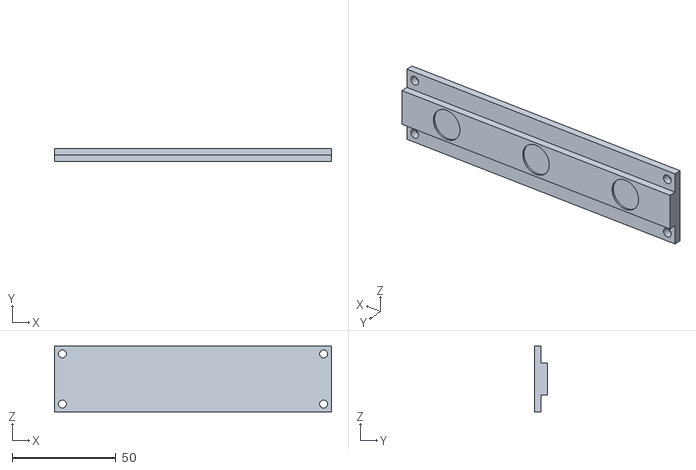
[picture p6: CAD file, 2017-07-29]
designs/stopcock-mount/stopcock-mount.stl
133.4 x 6.35 x 31.8

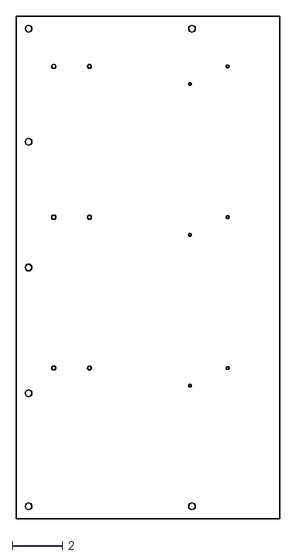
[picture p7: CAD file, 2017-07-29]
designs/backboard/backboard_left.dxf
10.5 x 20.0

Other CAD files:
designs/reservoir-stand/reservoir-stand.dxf

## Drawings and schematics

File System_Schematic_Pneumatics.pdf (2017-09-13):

## Module 4: Control Loading

# Universal Pneumatic Controller Setup Schematic

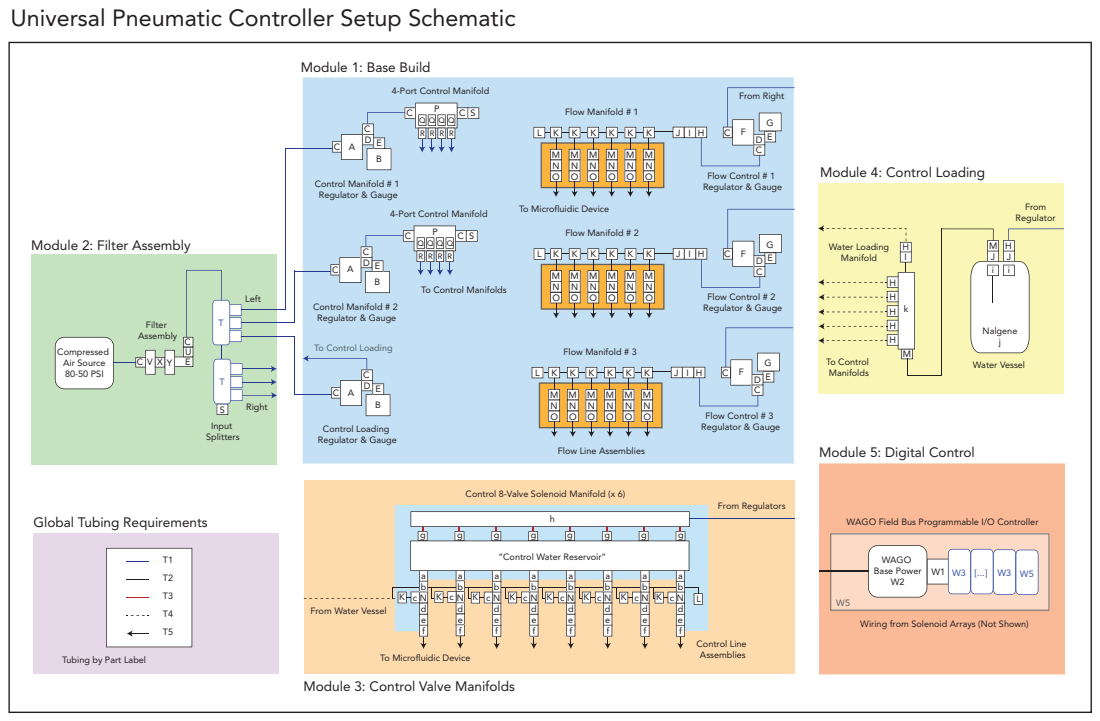
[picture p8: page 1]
Compressed Air Source 80-50 PSI; Filter Assembly; Input Splitters; Nalgene j; Water Loading Manifold; WAGO Base Power W2; Water Vessel; Control Line Assemblies; To Control Manifolds; From Regulator; Left; Right; From Regulators; Control Manifold # 1 Regulator & Gauge; Control Manifold # 2 Regulator & Gauge; Control Loading Regulator & Gauge; Flow Manifold # 3; Flow Control # 3 Regulator & Gauge; Flow Manifold # 2; Flow Control # 2 Regulator & Gauge; Flow Manifold # 1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

Module 1: Base Build

4-Port Control Manifold
QQQQ

To Microfluidic Device

Module 2: Filter Assembly

To Control Manifolds

To Control Loading

Flow Line Assemblies

Module 5: Digital Control

Control 8-Valve Solenoid Manifold (x 6)

Global Tubing Requirements

WAGO Field Bus Programmable I/O Controller

“Control Water Reservoir”

Wiring from Solenoid Arrays (Not Shown)

From Water Vessel

Tubing by Part Label

Module 3: Control Valve Manifolds

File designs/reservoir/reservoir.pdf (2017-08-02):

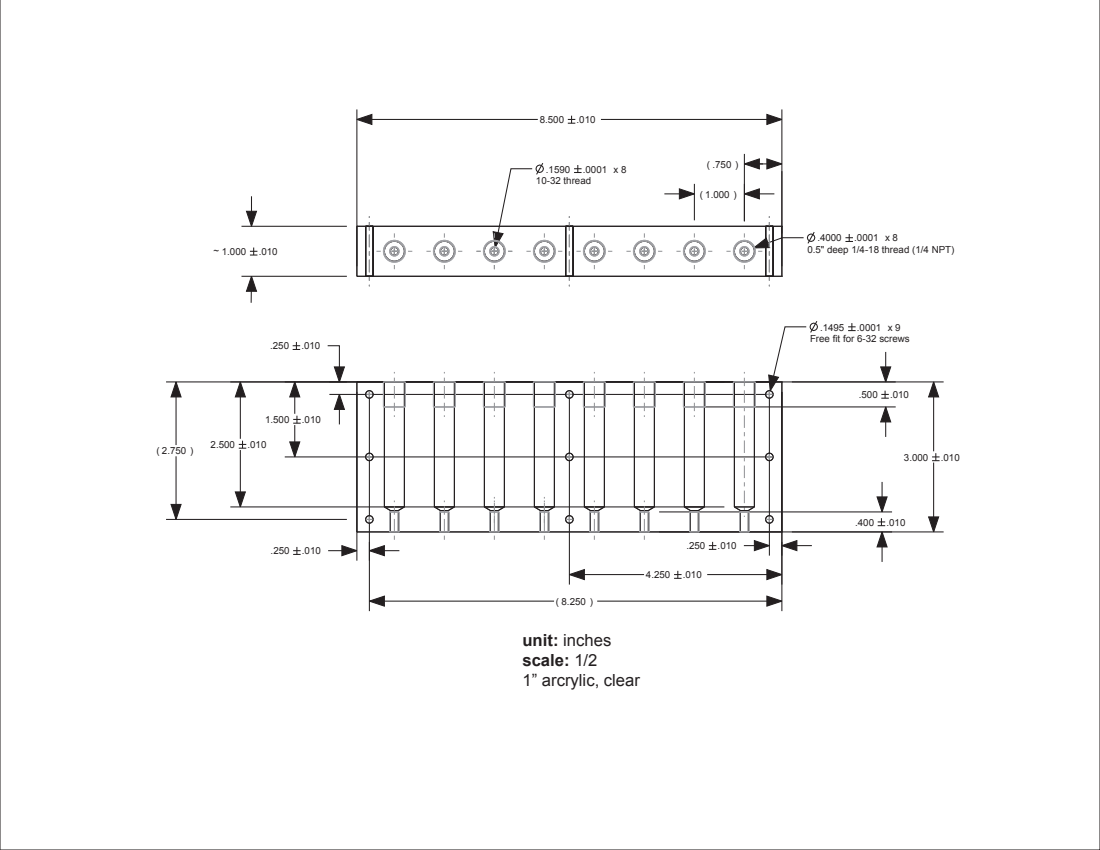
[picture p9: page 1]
10-32 thread; unit: inches scale: 1/2 1” arcrylic, clear

0.5" deep 1/4-18 thread (1/4 NPT)

Free fit for 6-32 screws

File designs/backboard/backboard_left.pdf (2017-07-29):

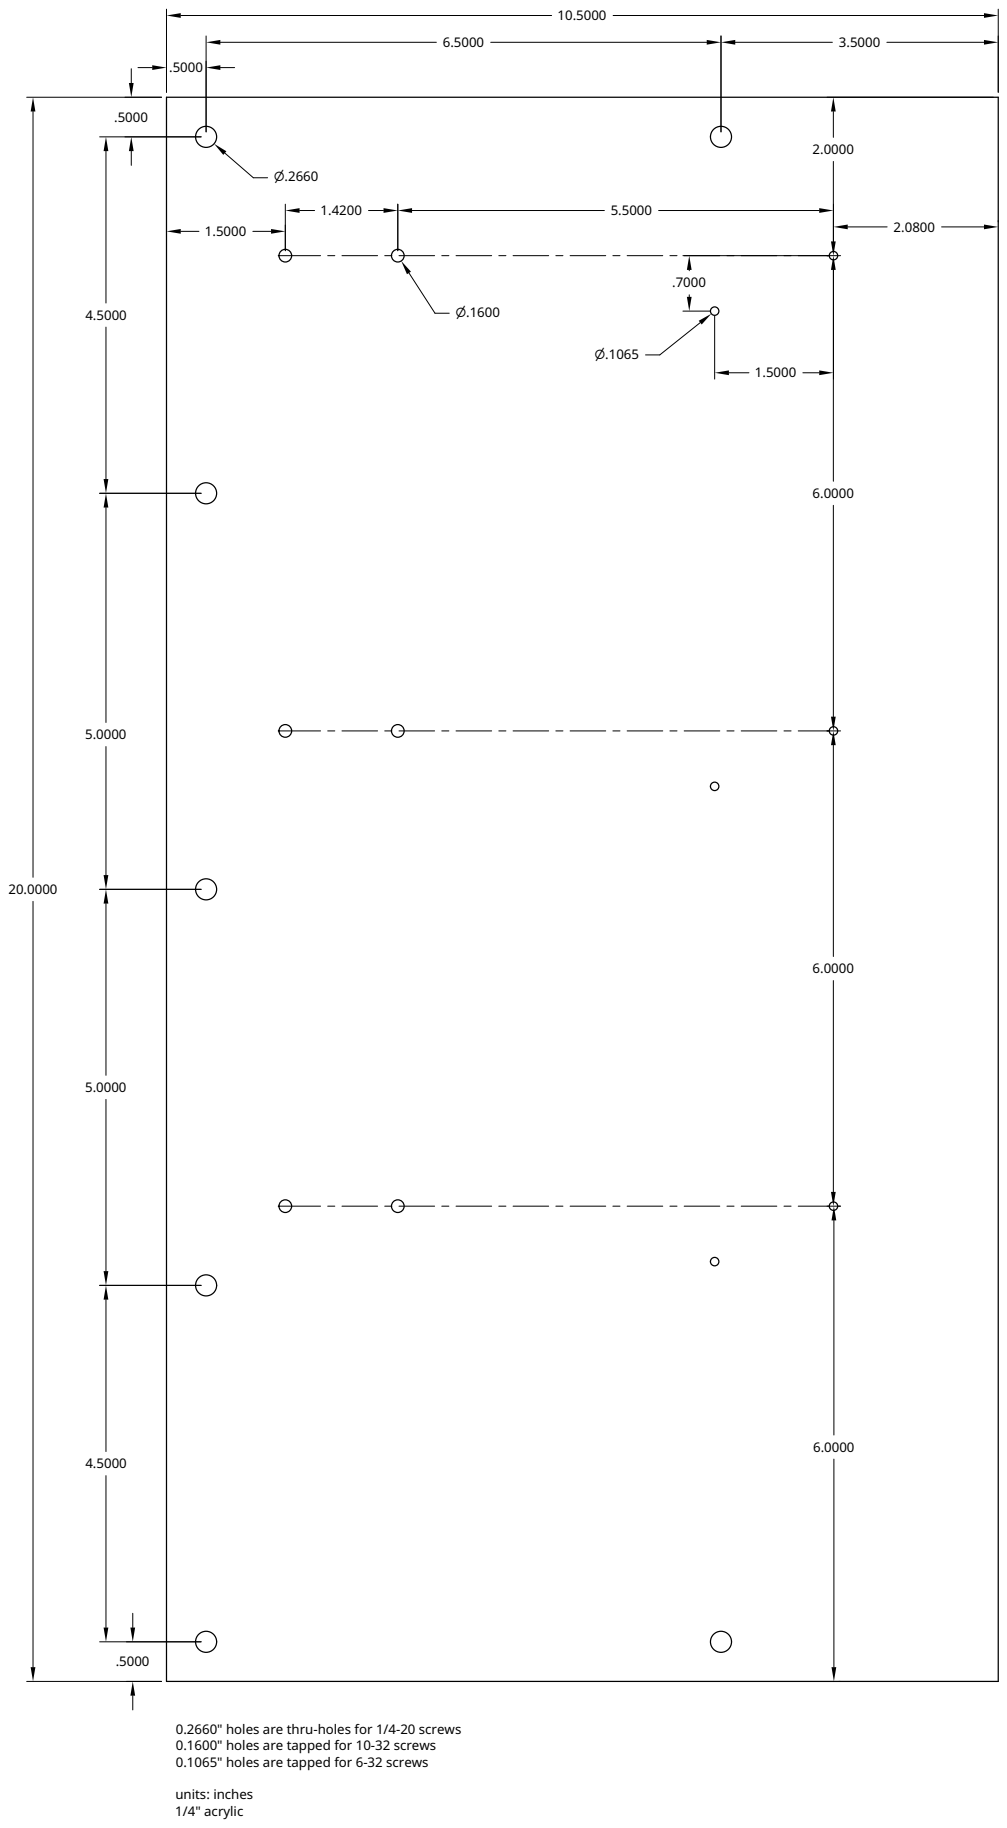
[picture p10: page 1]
units: inches 1/4" acrylic

0.2660" holes are thru-holes for 1/4-20 screws
0.1600" holes are tapped for 10-32 screws
0.1065" holes are tapped for 6-32 screws

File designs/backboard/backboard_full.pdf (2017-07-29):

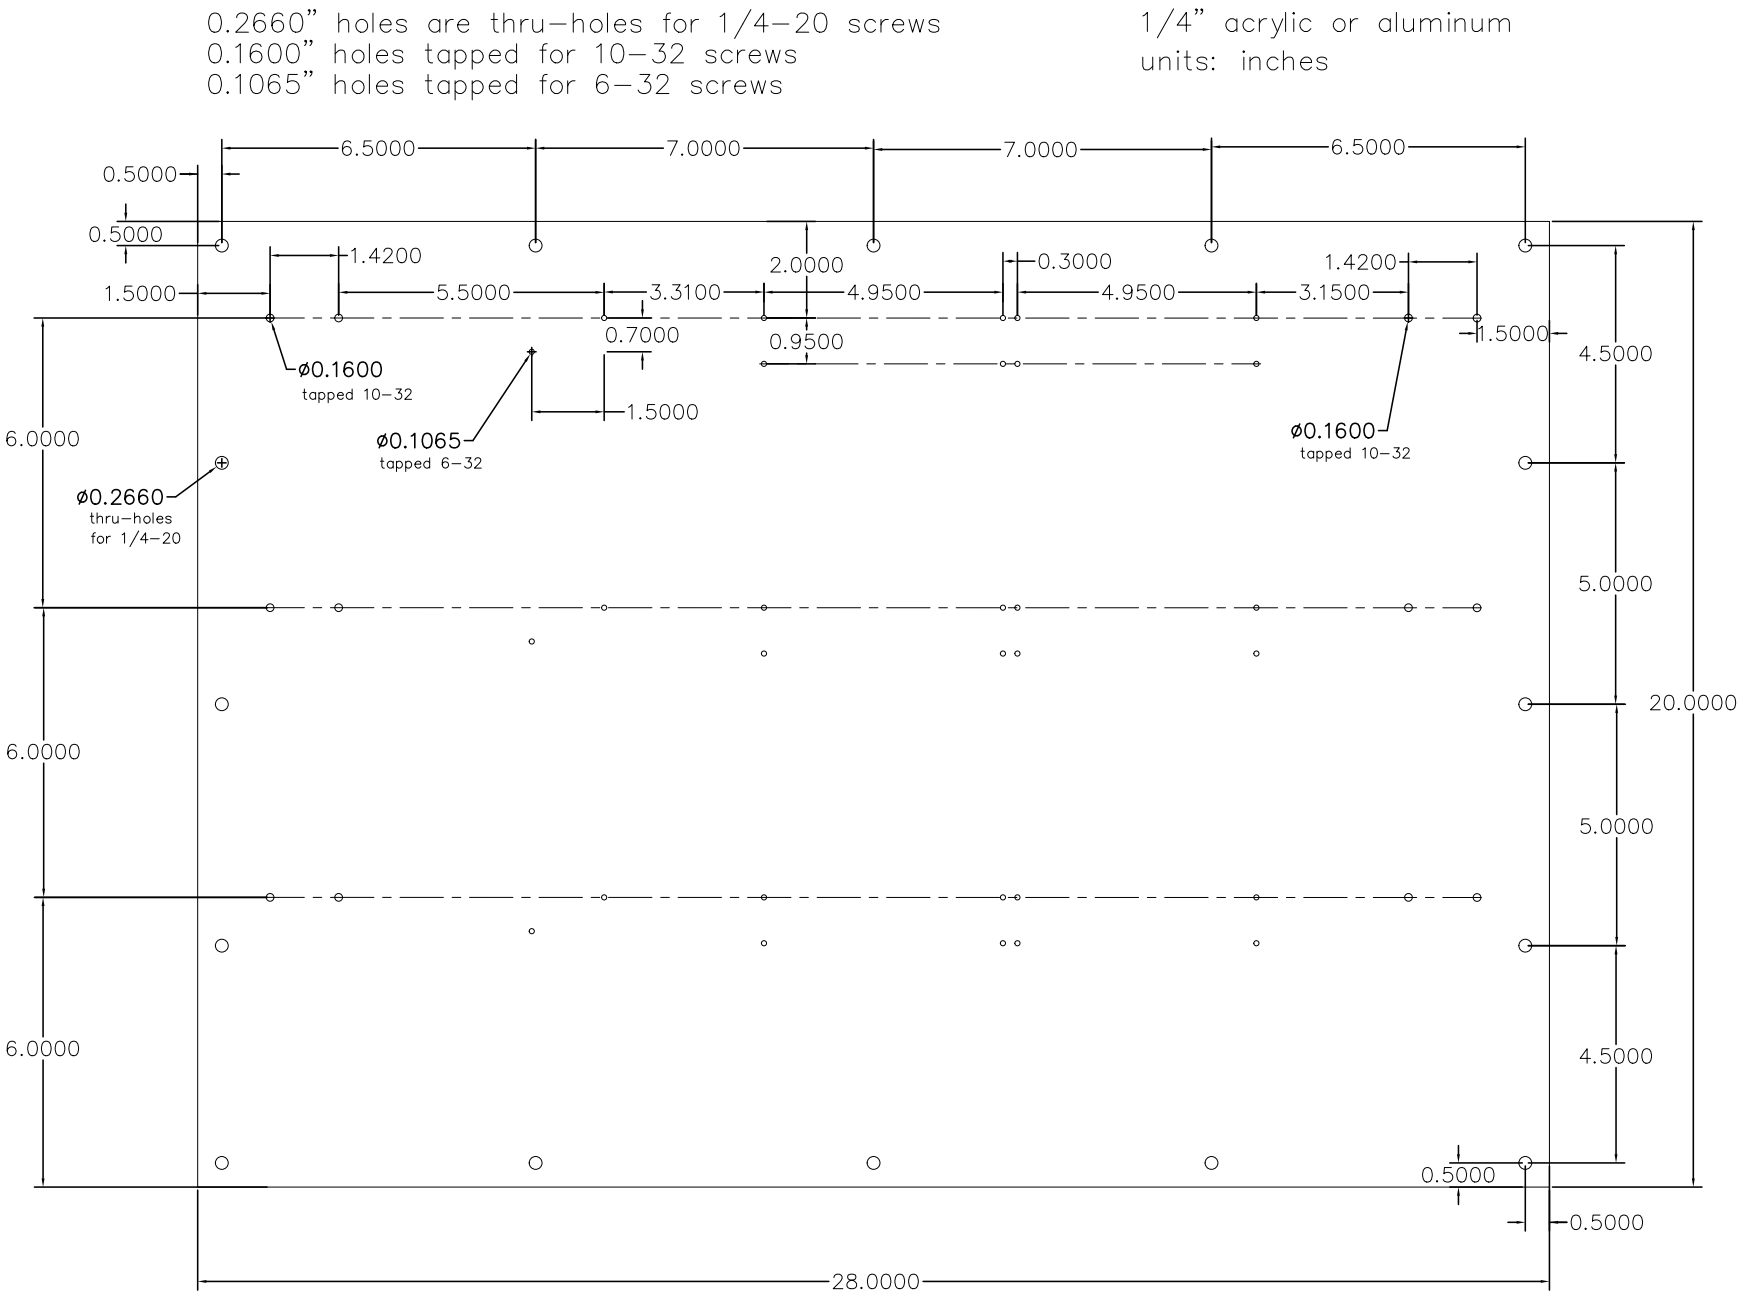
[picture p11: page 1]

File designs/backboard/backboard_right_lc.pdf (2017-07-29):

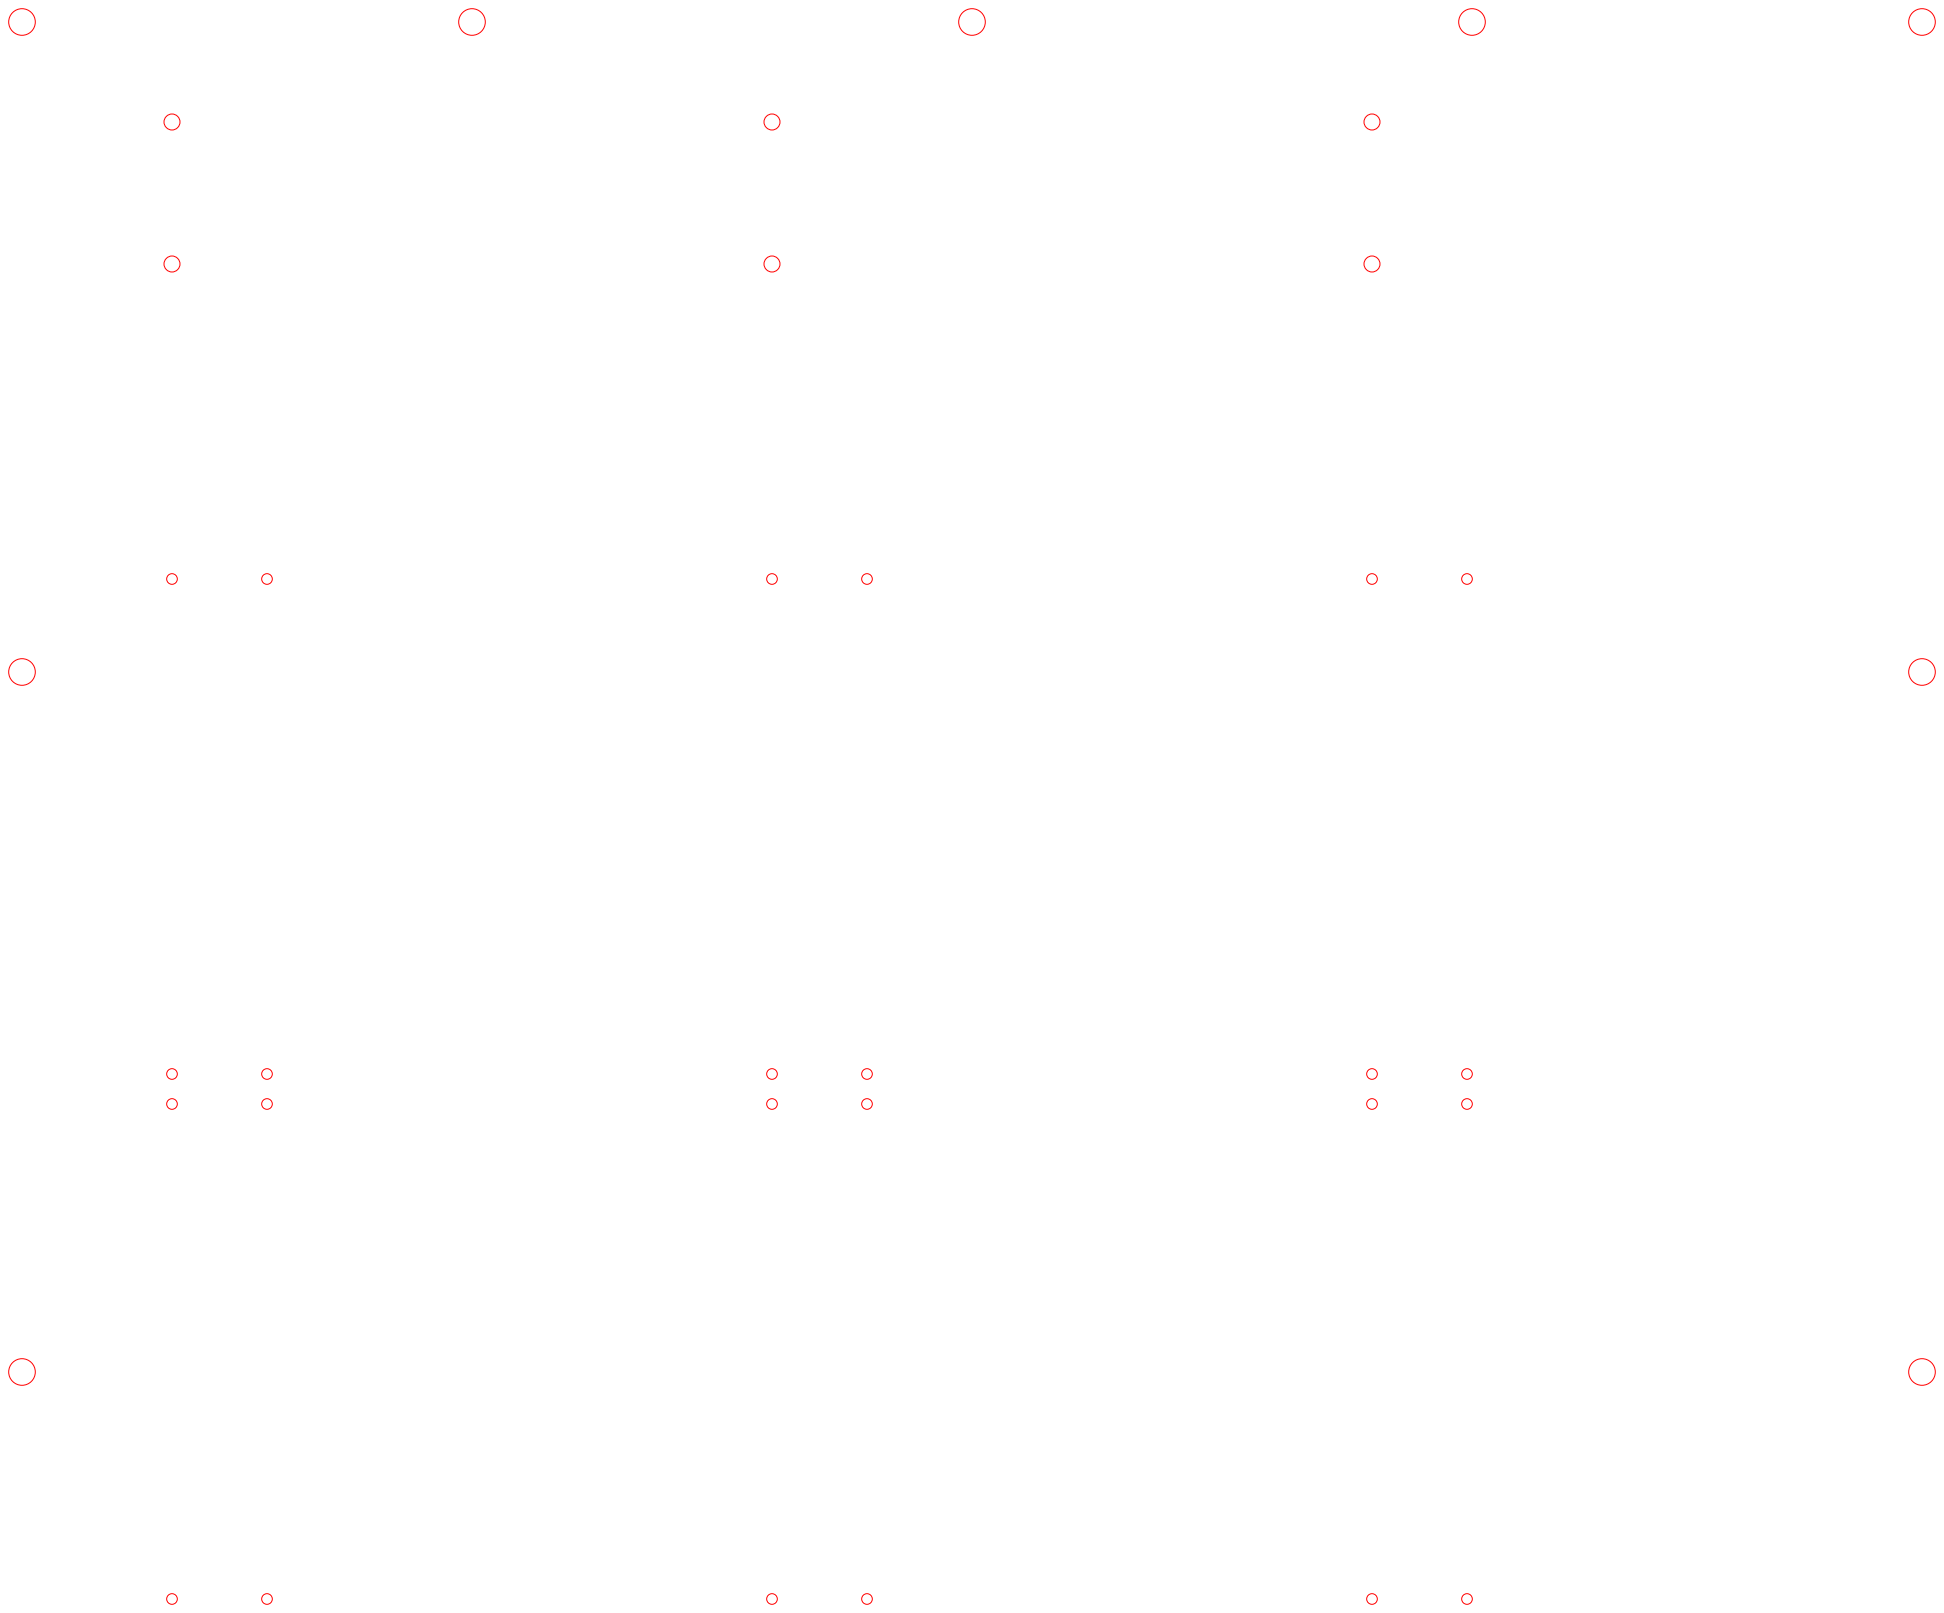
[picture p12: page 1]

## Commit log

2017-07-29 design files
    [backboard_full.dxf, backboard_left.dxf, backboard_right.dxf, reservoir-stand.dxf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]
2017-08-02 Changed '#6 screw' to '6-32 screw'
